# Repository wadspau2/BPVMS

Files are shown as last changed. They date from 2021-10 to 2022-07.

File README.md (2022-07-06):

# Breast Pump Vacuum Monitoring System ("Boobie Barometer")

This project was made for Allison Tolman (New Little Life) to test the vacuum performance of breast pumps. The project consists of a python script that interfaces with a controller, display, and pressure transducer. The project files also include STEP files for the 3D printed hardware.

<p float="left">
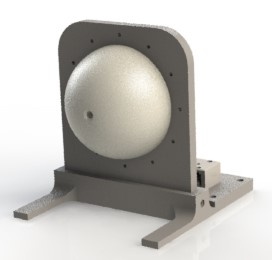
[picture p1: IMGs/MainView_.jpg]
  
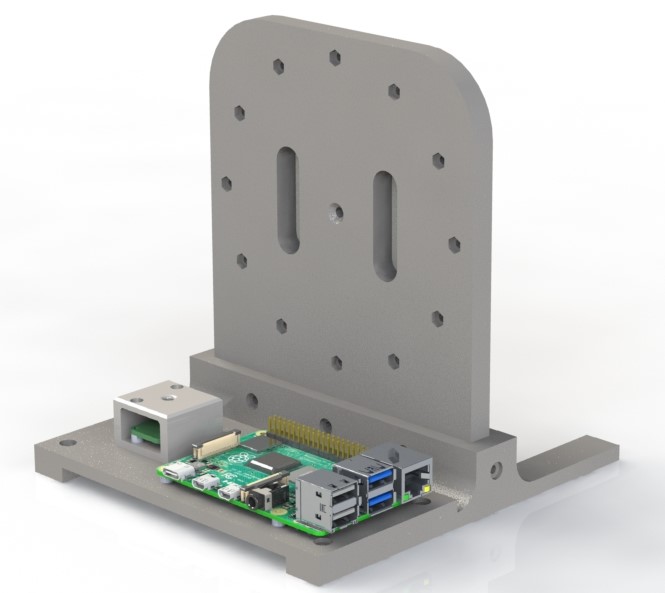
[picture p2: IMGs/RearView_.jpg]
  
</p>

## Hardware Description

### Materials
- Raspberry Pi 4 and power supply
- USB Stick
- Color TFT Bonnet + Joystick Add-on https://www.adafruit.com/product/4506
- STEMMA QT Cable https://www.adafruit.com/product/4210
- Adafruit LPS33HW Pressure Sensor w/ STEMMA QT https://www.adafruit.com/product/4414
- 3/32" ID, 5/32" OD Poly Tubing https://www.mcmaster.com/5648K23/
- Ecoflex 00-30 Super Soft Platinum Silicone https://www.amazon.com/gp/product/B00CA5VY3U/ref=ppx_yo_dt_b_asin_title_o03_s02?ie=UTF8&th=1
- CRC Silicone Mold Release Spray https://www.amazon.com/gp/product/B0013IZSDM/ref=ppx_yo_dt_b_asin_title_o03_s01?ie=UTF8&psc=1
- 2.5mm and 3mm Machine Screws
- 3mm nuts

### Assembly
1) All STP files are designed to be 3D printed in PLA or similar material.
2) Tap Raspberry Pi and Pressure Sensor mounting holes at 2.5mm. Tap all other holes at 3mm.
3) Smooth the inside of the ExternalMold piece, coat with mold release, and attach to the VerticalMount.
4) Place the tubing through the hole in the VerticalMount to the inside top surface of the ExternalMold piece.
5) Mix and pour the silicone into the ExternalMold cavity to create the soft interface. Let cure for recommended time.
6) Mount Raspberry Pi and Pressure Sensor as shown (see RearView_.jpg)
7) Connect Pressure Sensor to Raspberry Pi via the STEMMA cable. Insert the other end of the tubing into the pressure sensor.

## Usage

1) Power Raspberry Pi  
2) Insert the supplied USB stick (ensure that a folder titled 'data' exists on the home directory of the drive)  
3) Select 'Continue' to enter the main menu (selections are made by pressing down on the selector stick. Moving back in the menus is done by pressing left on the selector stick.)

### Main Menu

**Run Test**

The user has the option to select from three standardized test lengths (10s, 20s, and 30s) or perform a manual length test. The standardized tests will stop on there own, analyze the data, and produce graphs to the specified folder, indicated at the top of the screen, or they can be manually stopped by selecting 'Stop Test' at anytime during the test. The manual length test requires the user to end the test by selecting 'Stop Test'. Graphs, summary, and raw data are stored in the specified folder after each test.

**Change Units**

The user has the option to select which units are used in the data analysis and graph production. When first entering the menu, the current units being used are always highlited. When a user selects new units, the program automatically reverts back to the main menu.  

**Reset LPS35**

The user has the option to re-zero the pressure transducer in the event that the reading drifts away from zero by selecting 'Zero_LPS35'. The user can also specify the transducer to use an absolute measurement, however this is not recommended.  

**Eject USB**

The user must eject the USB stick prior to physically removing it from the Raspberry Pi. This is done by selecting this menu and removing the USB stick before hitting 'Continue' on the next screen. This will send the screen back to the initial screen which requires the USB stick to be reinserted in order to enter back into the main menu.  

**Shutdown**

The user must select 'Shutdown' prior to removing the power source from the Raspberry Pi. The next screen allows the user to abort the shutdown command within 3s if it was pressed by mistake. To restart the program and raspberry pi the user will have to unplug and plug in again the power supply.  

### USB Stick

The USB stick is keyed to the program and requires a folder titled 'data' at the top directory. Test folders can be removed from the data folder at will.

## Authors

* **Paul Wadsworth** - *Initial Work*

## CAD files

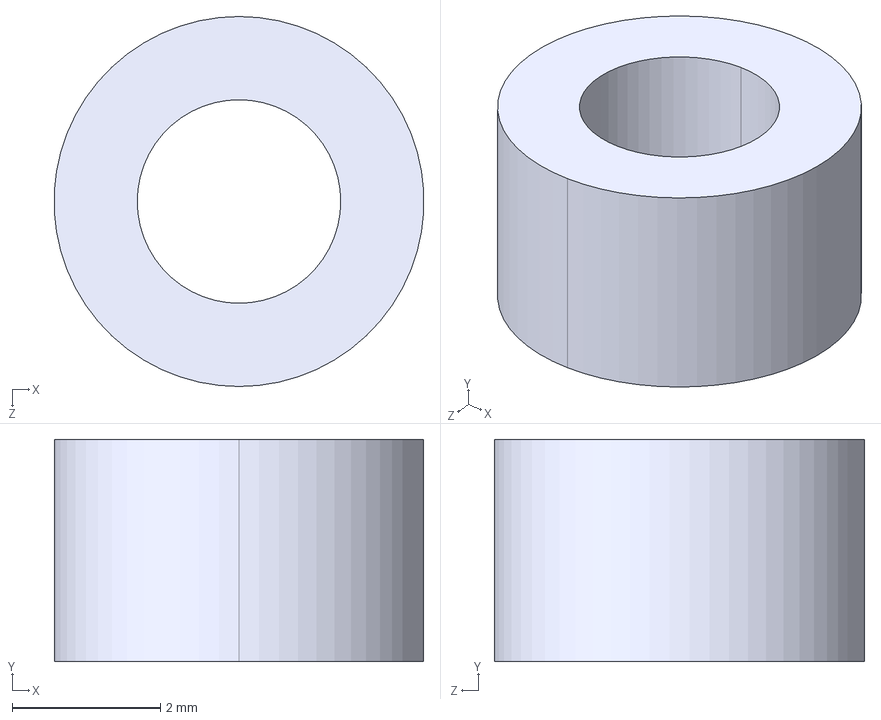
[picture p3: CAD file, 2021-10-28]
STEP Files/RaspberryPiSpacer.STEP
4.99 x 3.00 x 5.00 mm

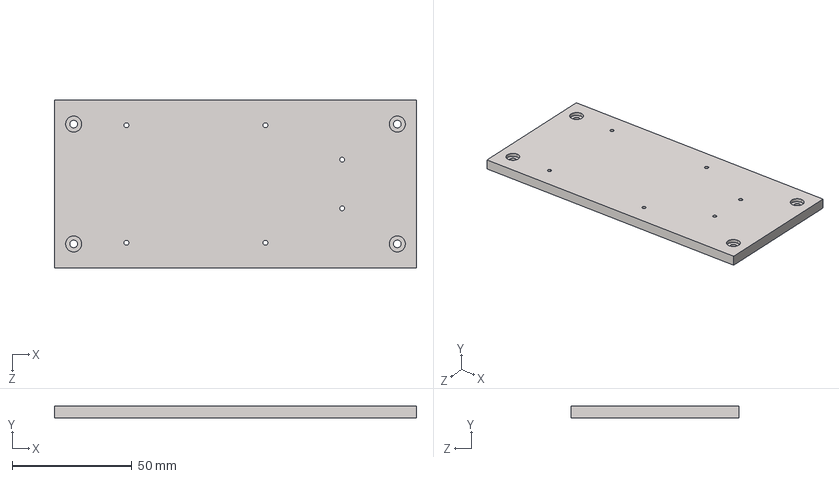
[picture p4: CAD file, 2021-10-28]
STEP Files/ElectronicsBed.STEP
151.0 x 5.00 x 70.0 mm

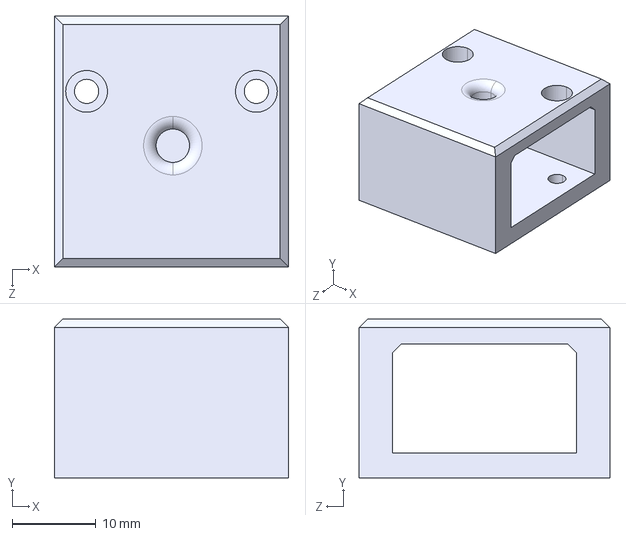
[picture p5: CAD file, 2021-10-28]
STEP Files/PressureSensorCase.STEP
28.0 x 19.0 x 30.0 mm

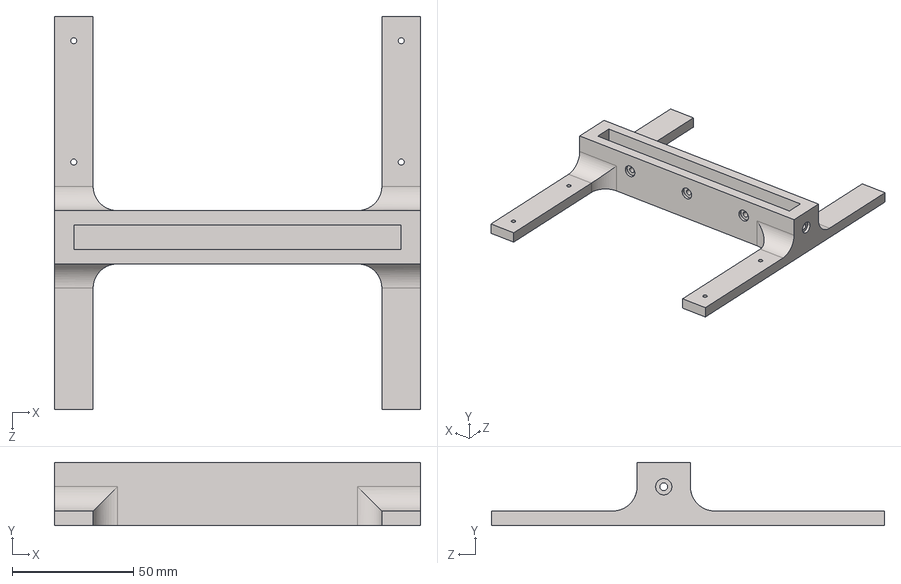
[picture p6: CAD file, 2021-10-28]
STEP Files/Stand.STEP
151.0 x 26.0 x 162.0 mm

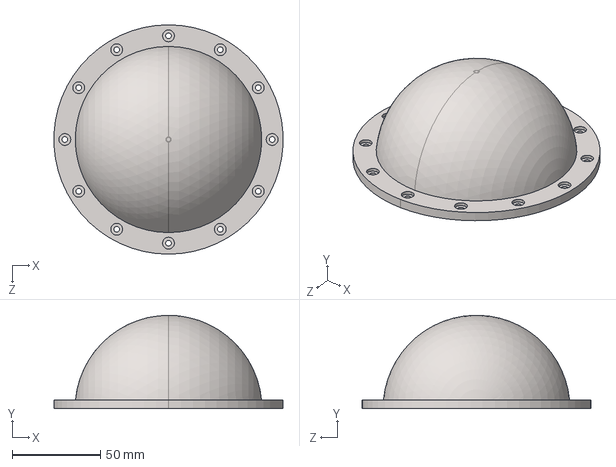
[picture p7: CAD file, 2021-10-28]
STEP Files/ExternalMold.STEP
129.8 x 53.0 x 130.0 mm

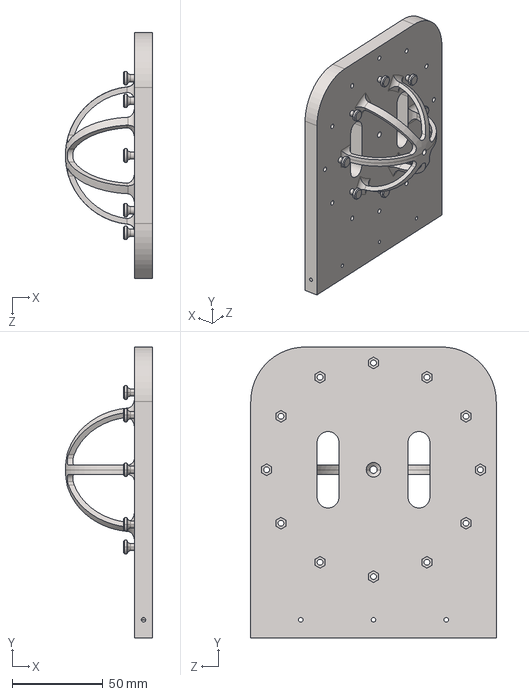
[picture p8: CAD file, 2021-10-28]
STEP Files/VerticalMount.STEP
47.9 x 160.0 x 135.0 mm

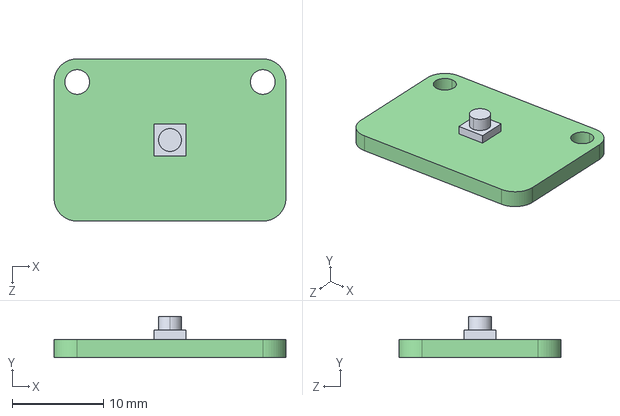
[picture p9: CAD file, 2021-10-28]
STEP Files/LPS35HW.STEP
25.4 x 4.50 x 17.8 mm

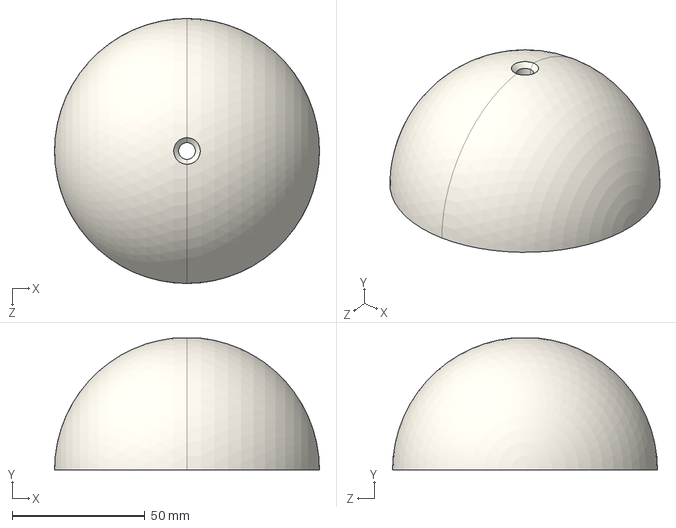
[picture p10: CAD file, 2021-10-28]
STEP Files/SiliconeMold.STEP
100.0 x 49.7 x 100.0 mm

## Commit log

2020-11-28 Current Units Indicator
2020-11-29 zero pressure test
2020-11-29 added current pressure reading
2020-11-29 fixed pressure units
2021-01-11 Increased Rate to 30hz
2021-01-11 Updated test rate to 30hz
2021-01-11 Updated pressure rate
2021-01-11 Updated pressure rate to 50hz
2021-01-11 Decreased Test Screen update Rate to 1hz
2021-10-28 Added STP CAD files
    [ElectronicsBed.STEP, ExternalMold.STEP, LPS35HW.STEP, PressureSensorCase.STEP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]
